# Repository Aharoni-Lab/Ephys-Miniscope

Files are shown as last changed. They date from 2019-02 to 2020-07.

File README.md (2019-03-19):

## Tutorial for assembling and using the integrated ephys Miniscope

Here we discuss the setup for the E-Scope. Below outlines the steps involved in assembling the head-mounted portion and DAQ portion of the system.

## Head-mounted E-Scope soldering and assembly

#### Components that need to be bought

* [Atmel ICE](https://www.digikey.com/products/en?mpart=ATATMEL-ICE&v=150) for programming the wire-free PCB
* Mill-Max 50mil male and female headers. You can get these from digikey.com and they are used to connect the INTAN PCB to the CMOS PCB. These are optional and generally should be skipped for mice.

#### Software to download
* Download [Atmel Studio](https://www.microchip.com/mplab/avr-support/atmel-studio-7). This will be used to program the microcontroller firmware onto the CMOS PCB.
* Downloaod the [Intan RHD2000 Interface Software](http://intantech.com/files/RHD2000interface_compiled_v1_5_2.zip). This will be used to connect and record ephys data.

### 1) Soldering wires to connect the CMOS PCB to the INTAN PCB

We first need to wire up 5 wires on the CMOS PCB. You should use very thing wiring for this (~0.25mm diameter conductors) since some of these connections will attach directly to the side pad of the serializer chip. You can use very thing "wire-wrap" wire which is single core or you can use mutlicore wire. Single core has the advantage of not splaying out but it is also less flexible. Once soldered, you should lay all 5 wires down across the top of the serializer and epoxy them (with a PCB safe glue/epoxy) so that no strain is applied to the solder connections. 

Below is a picture of the locations to solder the 5 wires. 
* D10 and D11 will carry the SSC Clock and SSC Data lines. 
* PCLK carries the pixel clock which will drive the SSC data protocol out of the INTAN PCB. 
* Finally, V+ and GND will provide power to the INTAN PCB.

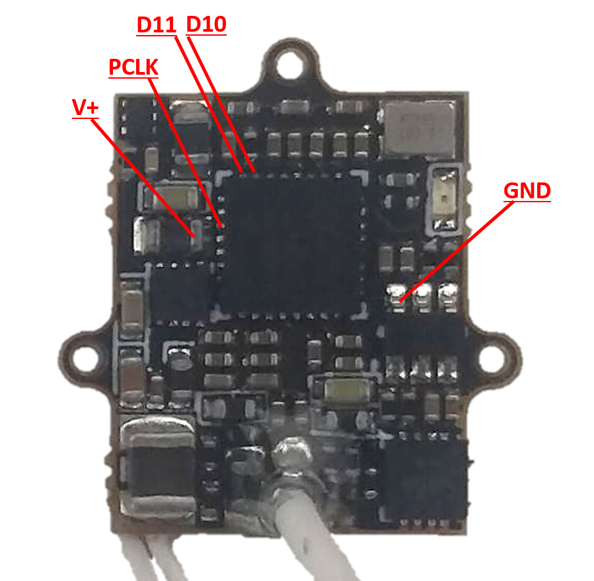
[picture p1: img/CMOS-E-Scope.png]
CMOS PCB wiring


### 2) Soldering wires onto the INTAN PCB

Now we need to solder the wires coming off the CMOS PCB onto the INTAN PCB. We have the choice to either directly solder these wires or to place a MillMax 50mil pitch header on these pads to connectorize them. For mice I would suggest directly soldering to minimize size and weight.

For connecting to the CMOS PCB v3.2 you will do the following connections (shown in the image below:
* GND connects to GND
* MCU V+ connects to V+
* INTAN V+ connects to V+
* SSC DATA connects to D10 or D11 (either is fine but keep this consistent across the E-Scopes you assemble
* LV can be left unconnected
* SSC Clock connects to PCLK
* SSC FRAME connects to D10 or D11 (use which ever one you didn't connect SSC DATA to)

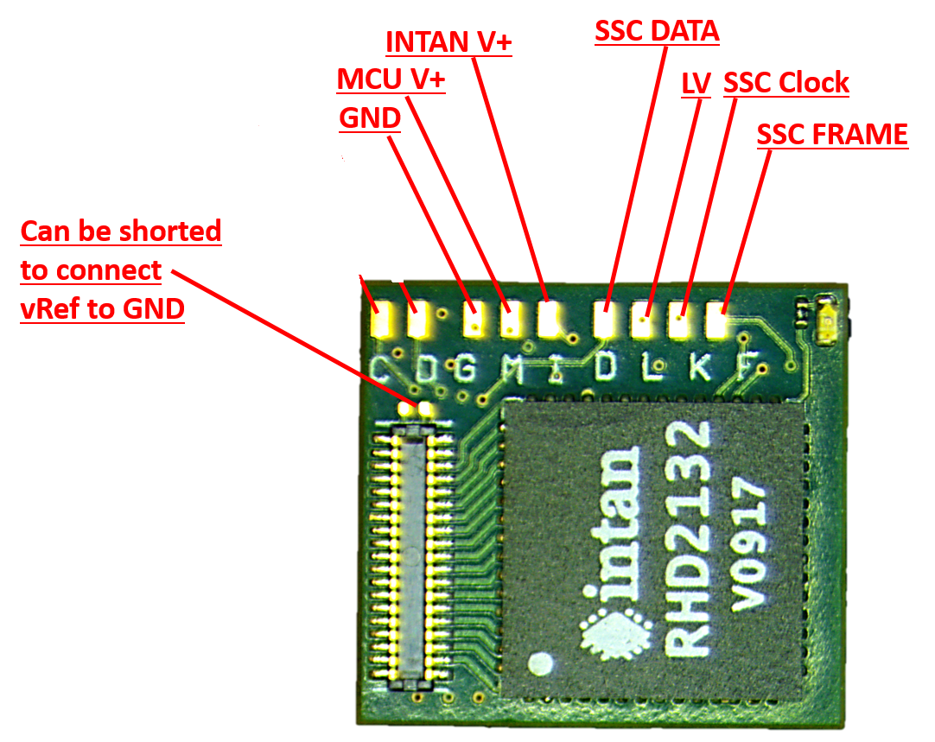
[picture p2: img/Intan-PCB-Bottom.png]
INTAN PCB wiring_bottom


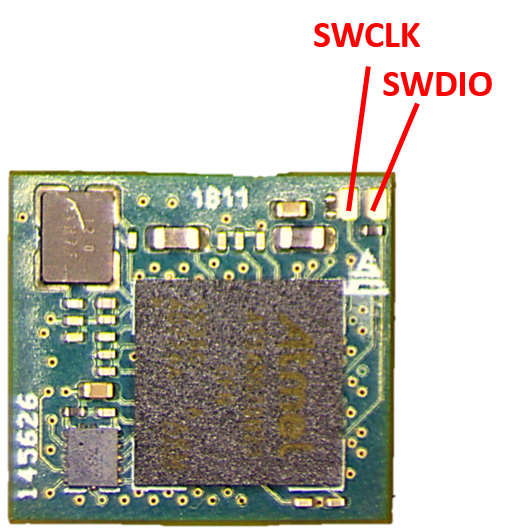
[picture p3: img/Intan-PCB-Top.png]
INTAN_PCB_wiring_top


### 3) Programming the MCU on the INTAN PCB

On one side of the INTAN PCB is the Intan RHD2132 chip and the other side is an ARM Cortex microcontroller (MCU). This MCU needs to be programmed once with the E-Scope firmware before it is functional. To do this we need to connect 4 lines to the INTAN PCB. This can, and maybe should, be done before completing step 2 above. The advantage of doing this programming step after completing step 2 above is the INTAN PCB can be powered through the coax cable and no additional power supply is needed.

You need to connect the following lines (refer to the images in step 2):
* SWCLK
* SWDIO
* MCU V+
* GND

These 4 lines need to be connected to an Atmel ICE which is the hardware necessary to program the MCU using an SWD protocol.
* In order to program the microcontroller on the INTAN  PCB, we first need to wire-up and connectorize a 4pin Mill-Max header to the 4 programming pins of the Atmel ICE programmer. These are GND, VTG (or V+), SWDIO, and SWDCLK. Below shows which pins/wires of the Atmel ICE have which function. The Atmel ICE has 2 different 5x2 pin ports. One is labeled AVR and one is labeled SAM. Either will work but depending on which one you are using it will change which column you refer to in the below chart.
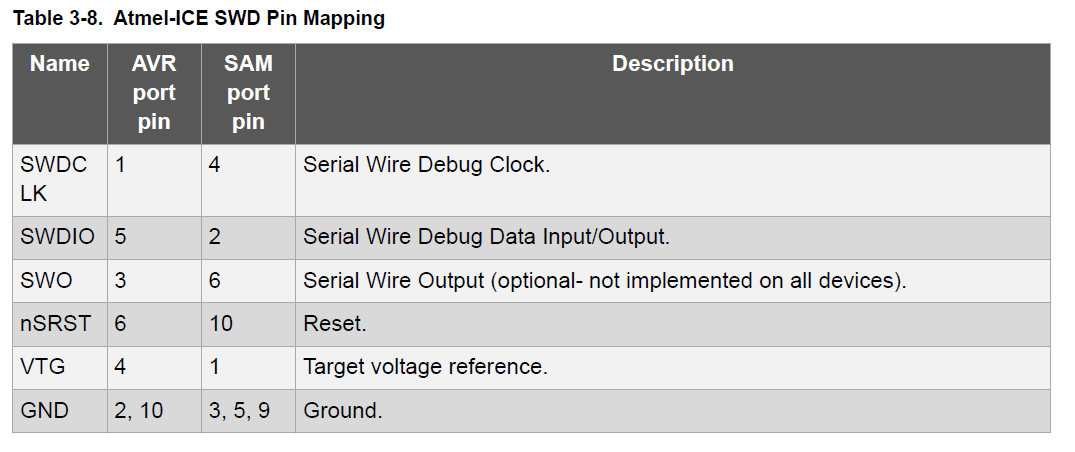
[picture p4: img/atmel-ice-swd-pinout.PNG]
Atmel ICE SWD pinout

* Connect the Atmel ICE to the programming header of the INTAN PCB.
* Power up the INTAN PCB throught either the coax cable (using the Miniscope DAQ) or directly connect 3.3V and GND from a power supply to the V+ and GND pads. 
* When the INTAN PCB gets powered on, you should see an orange light turn on on the Atmel ICE which shows that the Atmel ICE has detected voltage on the VTG (Voltage Target) pin.
* Open Atmel Studio and click the "Device Programming" button
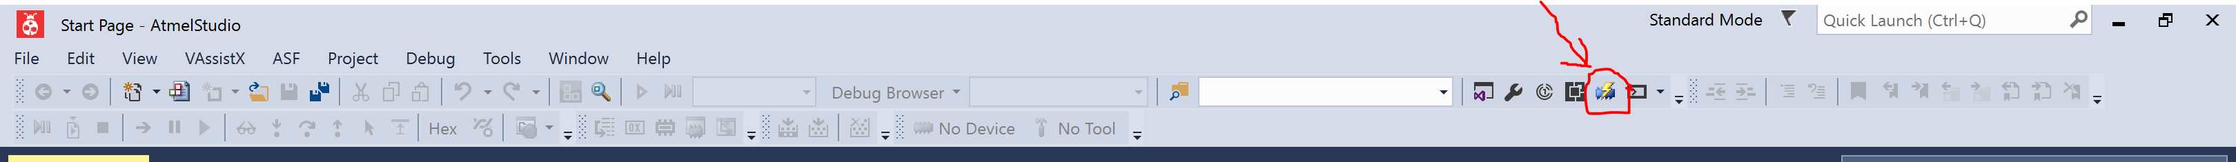
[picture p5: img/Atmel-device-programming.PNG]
Atmel Studio device programming buttone

* In the Device Programming window that pops up select:
  * Tool: Atmel ICE
  * Device: ATSAM....
  * Interface: SWD
  * Then click "Apply"
* Now check to make sure that Atmel Studio can communicate with the microcontroller on the INTAN PCB. You do this by clicking the "Read" button under Device Signature. If everything is powered and connected correctly you should see some numbers and letter pop up in the box and no error window show up. Now we are ready to program the microcontroller.
* Exit the Device Programming window.
* Now we have to do something a bit weird. I am not sure why this has to be done but it does. Open up the Atmel project found in the "/E-Scope-firmware" folder. This load up the code that makes up the INTAN MCU firmware. Now click "Debug" from the top menu bar and then click "Start Debugging and Break". Wait about 15 seconds while the debugger does its thing in Atmel Studio and then the code should jump to the "main()" function and highlight it. Now click the play button (labelled "Start Debugging") in the top menu. Wait a few seconds then click the stop button (labelled "Stop Debugging"). 
* Go back to the "Device Programming" window by clicking the "Device Programming" button.
* Click "Memory" on the left menu panel of the Device Programming window we are currently in.
* Click "Browse" and locate the E-Scope firmware. This is a .hex file you can find in the "/E-Scope-firmware" folder.
* Click "Program". This will erase, program, and verify the microcontroller. It will tell you if everything was successful.
* Now the microcontroller on the INTAN PCB knows how to be a wire-free Miniscope microcontroller.

## Miniscope DAQ E-Scope soldering and assembly

We now need to modify the standard Miniscope DAQ to be able to handle and transmit the ephys data from the E-Scope. We will do this by soldering 4 wires onto the DAQ PCB which will send the ephys data from the Miniscope DAQ to our SSC to INTAN LVDS PCB. We will roughly be following the following schematic:

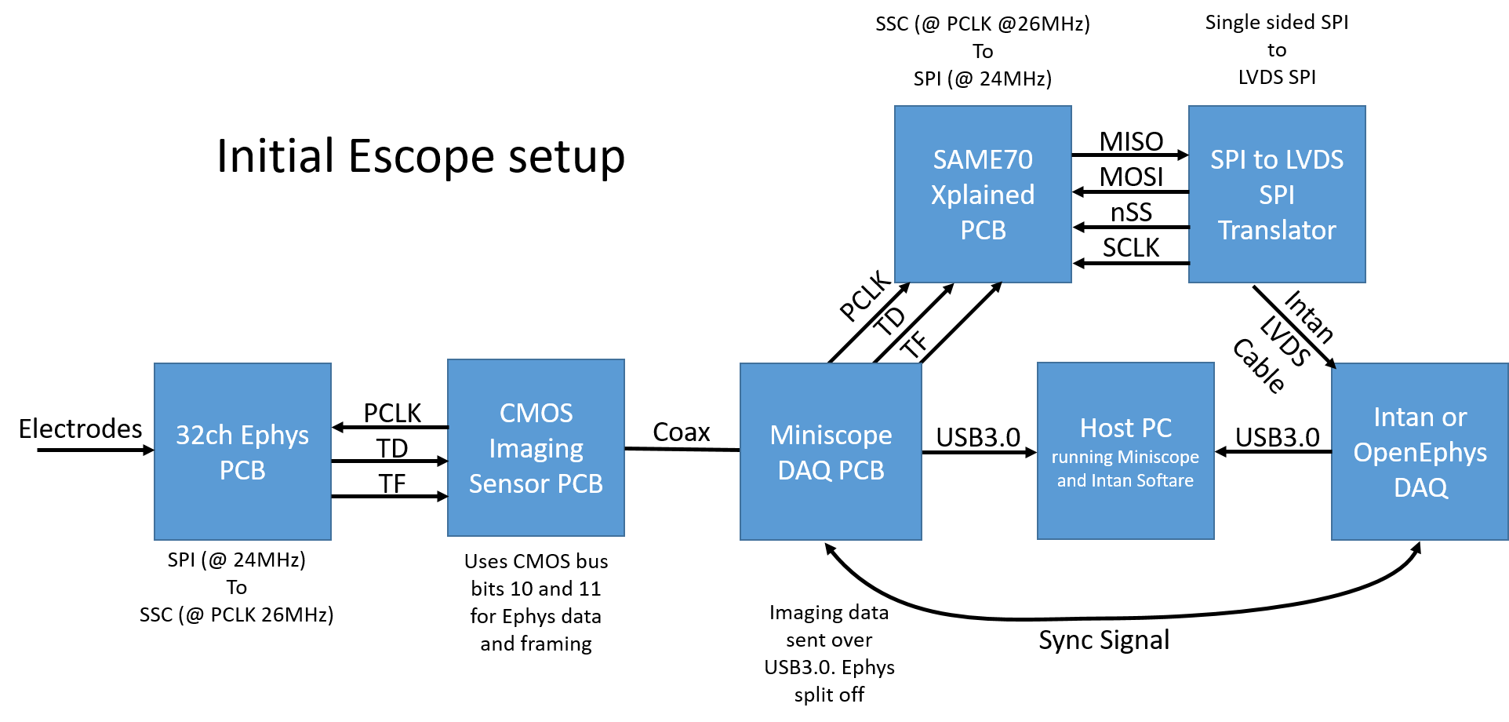
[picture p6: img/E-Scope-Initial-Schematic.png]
E-Scope Schematic


As you can see from the schematic, these wires coming off of the Miniscope DAQ PCB will connect to hardware that basically undoes the SSC data protocol implemented by the MCU on the INTAN PCB and make an Intan DAQ think that it is talking directly to an Intan headstage.

### 1) Wire up the Miniscope DAQ PCB

Similar to what we did for wiring up the CMOS PCB, we need to wire up some lines for SSC DATA, SSC Clock, SSC FRAME, and power. See image below for which pads to solder to. Use the same wire as you used to wire up the CMOS PCB and epoxy these wires down to the DAQ PCB to remove any strain on the solder joints.

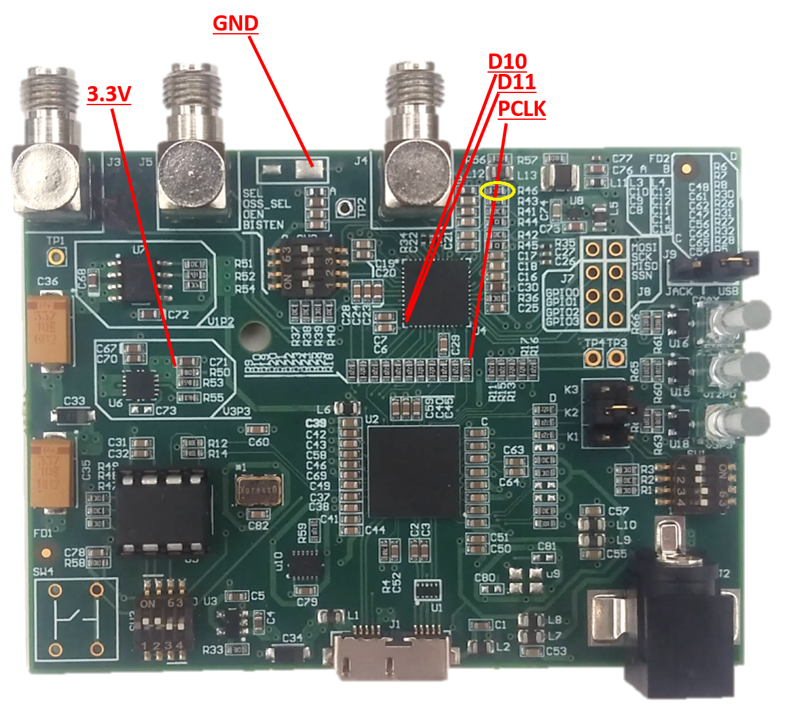
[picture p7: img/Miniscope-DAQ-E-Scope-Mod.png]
Miniscope-DAQ-E-Scope-Mod


You definitely need to solder up D10, D11, PCLK, and GND. The need for the 3.3V connection will depend on which version of the system you are using. You might as well just solder this one up as well.

### 2) Change the Miniscope DAQ Deserializer Mode from 10 bits to 12 bits

We need to remove one resistor on the Miniscope PCB and short then now empty pads together . This resistor is responsible for change the Deserializer from using 10bit mode to 12bit mode. We need to do this because the CMOS imaging sensor uses the bottom 10 bits of the SERDES and the Ephys data uses the top 2 bits (TD, TF which are on pins D10 and D11). So **remove resistor R46 (which is circled in yellow above)** which is near the top of the PCB to the right of the SMA connector that goes to the head-mounted scope. Once you remove this resistor, we need to short the 2 open pads together which effectively changes this resistance to 0 ohms. You can build up a solder ball that spans these 2 pads, solder a short piece of metal across these 2 pads, or solder a 0ohm resistor in the R46 location. I recommend the last option.

### 3) Connect the Miniscope DAQ PCB to SSC-2-INTAN-LVDS PCB

Alright, we are almost done here. The ephys data coming out of the wires we soldered onto the Miniscope DAQ need to get converted to a data protocol an Intan DAQ understands. We do this using our custom SSC-2-INTAN-LVDS PCB. This PCB receives SSC (RF,RT,RK) and converts it to an LVDS SPI to be sent out over a 2x6 omnetics connector at the top of the PCB to an Intan or OpenEphys DAQ. Below is a rendering of this PCB.

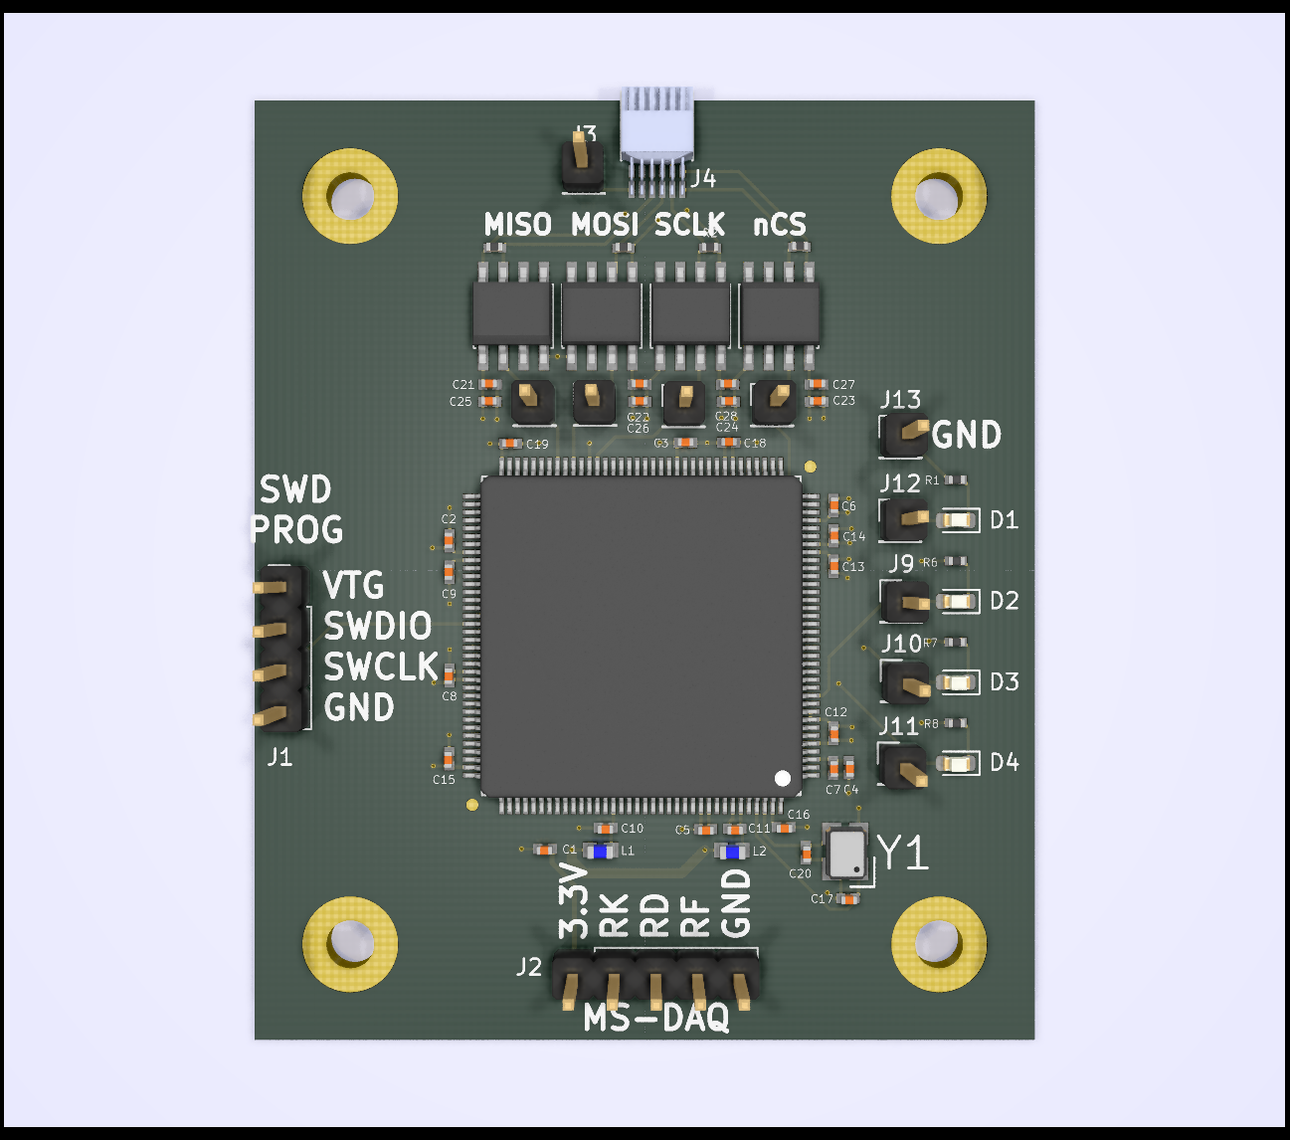
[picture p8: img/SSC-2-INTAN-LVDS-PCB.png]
SSC-2-INTAN-LVDS


At the bottom of this board is a 5 pin 100mil pitch header for connecting it to the Miniscope DAQ. I would suggest soldering a right angle header to this PCB pointing down. On the Miniscope DAQ, you can epoxy another 5 pin header to the edge of the PCB so that these 2 PCBs can be easily connected. The connections need to be the following:

**NOTE**

**For the original version of this PCB, the labelling is incorrect.** The order should 3.3V, RD, RF, RK, GND and not 3.3V, RK, RD, RF, GND.

| SSC-2-INTAN PCB | Miniscope DAQ PCB |
| --- | --- |
| GND | GND |
| 3.3V | 3.3V |
| RK | PCLK |
| RD | D10 or D11. Whichever one was connected to TD on the 32 channel Ephys PCB|
| RF | D10 or D11. Whichever one was connected to TF on the 32 channel Ephys PCB |

### 4) Program the MCU on the SSC-2-INTAN-LVDS PCB

Out last step is to program this PCB so it knows what it is suppose to do. Here we follow the same procedure we did above for programming the 32 Channel Ephys PCB. The programming header on the SSC-2-INTAN-LVDS PCB is on the left and includes the 4 connections you need access to through a 100mil pitch header. These are VTG (which will tell the Atmel ICE programmer to program the MCU at 3.3V), SWDIO, SWCLK, and GDN. Follow the steps above but program this MCU with the SSC-2-INTAN-LVDS firmware .hex file. This PCB needs to be powered up when programming which is done through the bottom 'MS-DAQ' 5 pin header by supplying 3.3V and GND. If you already have this hooked up to the Miniscope DAQ all you should need to do is power up the Miniscope DAQ and it should in turn power on this PCB.

## Hook everything up and test the system

We should now be done with all the hard work. All that is left to do is connect everything together and make sure we are getting correct data from the system. The overall layout should be:

32 Channel Ephys PCB -> CMOS sensor PCB -> coax -> Miniscope DAQ -> SSC-2-INTAN-LVDS PCB -> Intan or Open Ephys DAQ

All the power on all of these PCBs is floating which apperently introduces a ton of noise. **To fix this we need to connect building ground to the ground of the Miniscope system. This can be most easily done (be careful) by plugging in only the ground pin of an electrical cord into a wall electical socket and then clip the other end of the ground wire of the cable to the pin labeled 'GND' on the SSC-2-INTAN-LVDS PCB. Do this before powering everything up.**

Once you have connected building ground you can plug in the USB cable of the Miniscope DAQ and the USB cable and power jack of the Intan DAQ. Now open up the Intan DAQ software on the computer and make sure it detects the Intan DAQ and a 32 channel headstage. Right now the Intan DAQ thinks it is talking to an Intan headstage but it is actually talking to the SSC-2-INTAN-LVDS PCB. If you leave the coax cable unconnected from the Miniscope DAQ you will see placeholder data show up in the Intan DAQ software. This should look like DC voltages on all 32 channels with channel 0 having the lowest voltage and channel 31 having the highests. Once the head-mounted Miniscope coax cable is connected, this placeholder data gets replaced with real ephys data.

**A few important notes:**

* Generally you will want the ephys and imaging synced together. This is done by connecting one of the Intan DAQ digital input ports to the SYNC output of the Miniscope DAQ (which is the SMA connector labeled J5). Make sure to enable this digitial input pin in the Intan DAQ software. This will result in the Intan DAQ recording the SYNC signal from the Miniscope DAQ which will allow us to sync all the data offline. If you do this, **make sure to always start the Intan DAQ software recordinging before you start the Miniscope DAQ software recording.**

**Order of connecting and powering up the system**

* Hook up ground of the DAQ system to building ground
* Connect the Miniscope to Miniscope DAQ using the coax cable
* Hook up the DC power supply on the Intan DAQ
* Hook up the two USB cables. One for the Miniscope DAQ and one for the Intan DAQ
* Make sure that the sync cable is connected (Cable that connects the Intan board with the Miniscope DAQ)
* Open up Intan DAQ software and Miniscope DAQ software
* In the Intan software, click "Board Digital Inputs" radio button. Then turn on LOGIC DIN-00.
* Check everything is running correctly by clicking the "Runn" button in the Intan software and by connecting to the Miniscope using the Miniscope DAQ software.

**When ready to record**
* In the Intan software, click the "Select Vase Filename" button and name the ephys recording file.
* Click record in the Intan software
* Click record in the Miniscope DAQ software
* Do your recording
* Stop recording with the Miniscope DAQ software
* Stop recording with the Intan software

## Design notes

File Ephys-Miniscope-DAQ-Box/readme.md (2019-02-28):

3D printer model for Ephys-Miniscope DAQ box

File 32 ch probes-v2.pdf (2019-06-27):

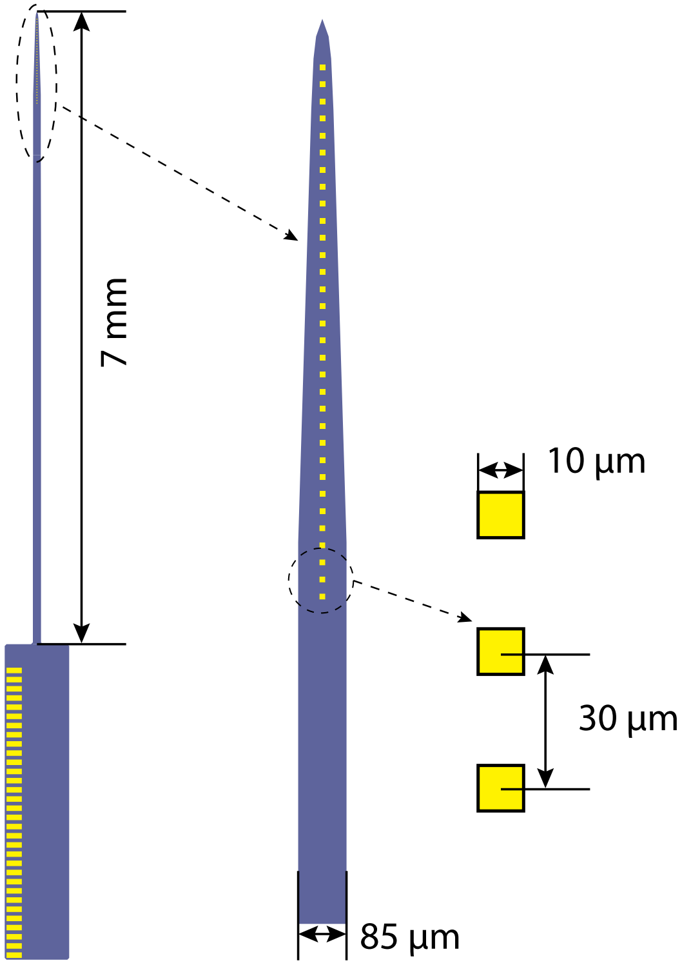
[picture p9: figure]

32ch probe geometry

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
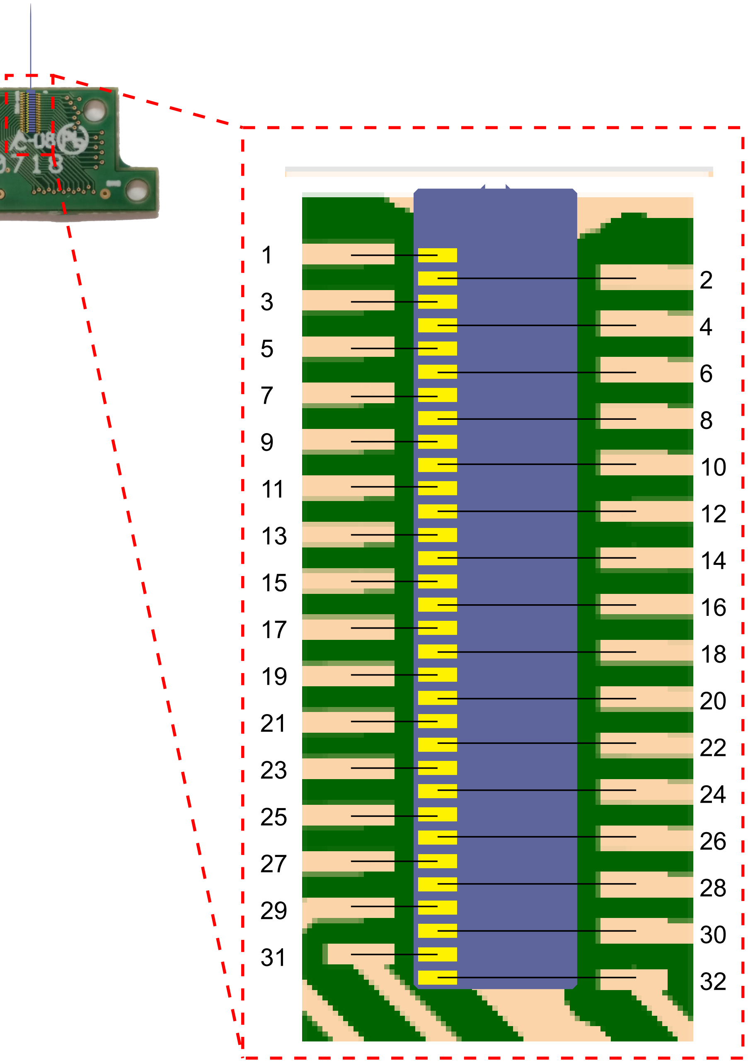
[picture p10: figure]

Channel number definition and corresponding Pin number

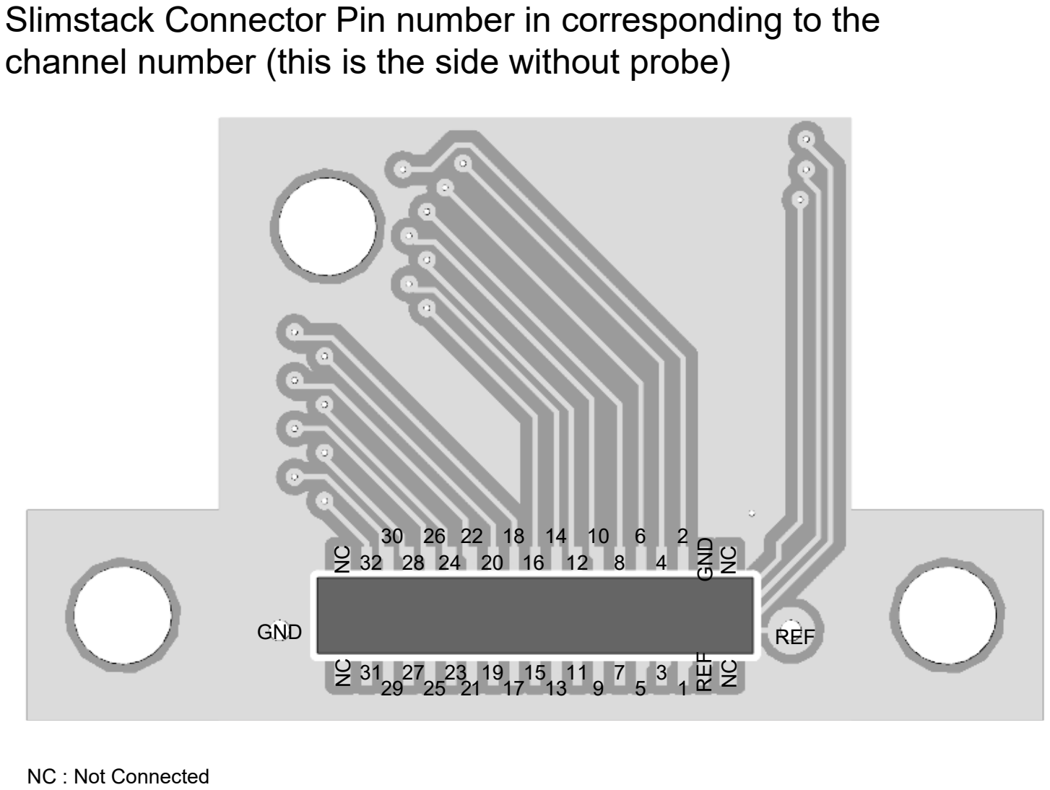
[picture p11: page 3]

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
GND | REF

Slimstack Connector Pin number in corresponding to the channel number (this is the side without probe) NC NC NC NC

NC : Not Connected

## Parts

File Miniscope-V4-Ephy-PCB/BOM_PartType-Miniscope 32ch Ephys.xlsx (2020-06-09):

Comment | Manufacture Part Number | Digikey Part Number | Description | Designator | Footprint | LibRef | Quantity | Value
Capacitor | GRM155R60J475ME47D | 490-5915-1-ND | Generic SMD Capacitor | C1, C3 | CAPC100X50X60L25N | Capacitor | 2 | 4.7uF
Capacitor | GRM033R61A104ME15D | 490-5405-1-ND | Generic SMD Capacitor | C2, C4, C5, C6, C7, C9, C10, C12, C13, C16 | CAPC60X30X33L15L | Capacitor | 10 | 100nF
Capacitor | GRM033R61A105ME15D | 490-13226-1-ND | Generic SMD Capacitor | C8 | CAPC60X30X33L15L | Capacitor | 1 | 1uF
Capacitor | GRM033R71A103KA01D | 490-3194-1-ND | Generic SMD Capacitor | C14, C15 | CAPC60X30X33L15L | Capacitor | 2 | 10nF
Capacitor | GRM0335C1H120JA01D | 490-6114-1-ND | Generic SMD Capacitor | C17, C18 | CAPC60X30X33L15L | Capacitor | 2 | 12pF
LED | VLMS1500-GS08 | VLMS1500-GS08CT-ND | LTST-C191KRKT | D1 | 0402 LED | LXZ1-PR01 | 1
34Pin Connector | 5046223410 | WM10896CT-ND | 34Pin Connector | J1 | 504622-3410 | 16x2 Pin Molex | 1
Inductor | BLM18PG471SN1D | 490-5223-1-ND | Generic SMD Inductor | L2, L3 | INDC160X80X95L40L | Inductor SMD | 2 | 470 Ohms @ 100MHz
Res1 | DO NOT LOAD | DO NOT LOAD | Generic SMD Resistor | R1 | RESC60X30X26L15L | Resistor | 1 | DNL
Res1 | ERJ-1GEF2002C | P20.0KABCT-ND | Generic SMD Resistor | R2 | RESC60X30X26L15L | Resistor | 1 | 20kOhm
Res1 | ERJ-1GEF1003C | P100KABCT-ND | Generic SMD Resistor | R3, R4 | RESC60X30X26L15L | Resistor | 2 | 100kOhm
Res1 | RC0201FR-07499RL | YAG2700CT-ND | Generic SMD Resistor | R5 | RESC60X30X26L15L | Resistor | 1 | 499Ohm
SAMS70N21 | ATSAMS70N21A-CFNT | 1611-ATSAMS70N21A-CFNTCT-ND | SAMS70N21 ARM Cortex-M | U1 | VFBGA100CP65_10X10_700X700X100B32L | SAMS70N21 | 1
RHD2132 | RHD2132. I will supply this component | I will supply this component | Intan Technologies RHD2132 | U2 | QFN57P50_800X800X85L40X23T610L | RHD2132_QFN | 1
ABM8G-12.000MHZ-4Y-T3 | ABM8G-12.000MHZ-4Y-T3 | 535-10901-1-ND | ABM8G-12.000MHZ-4Y-T3 | U3 | ABM8G-12.000MHZ | ABM8G | 1
TXB0304 | TXB0304RUTR | 296-29682-1-ND | TXB0304 4ch bidir. level shift 100Mbps | U4 | QFN12 | TXB0304 | 1

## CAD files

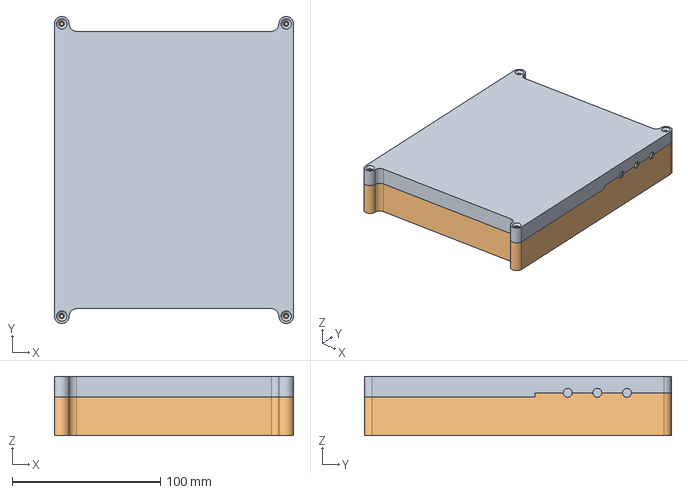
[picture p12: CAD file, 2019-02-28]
Ephys-Miniscope-DAQ-Box/Board Base v30.step
161.3 x 207.0 x 40.0 mm

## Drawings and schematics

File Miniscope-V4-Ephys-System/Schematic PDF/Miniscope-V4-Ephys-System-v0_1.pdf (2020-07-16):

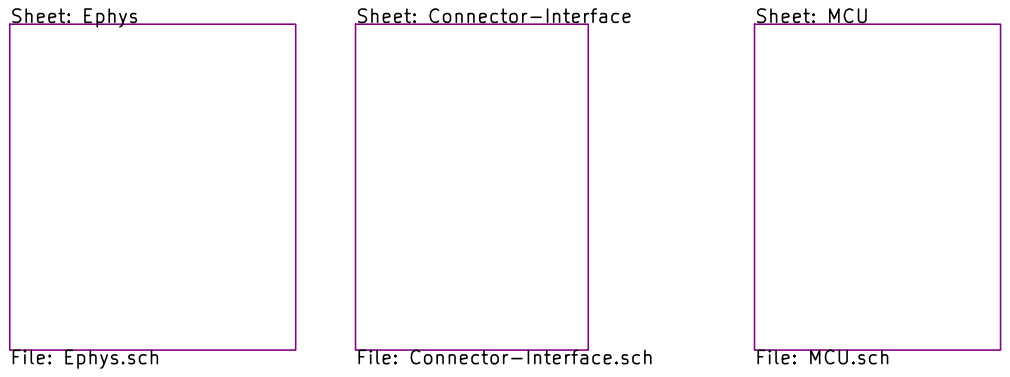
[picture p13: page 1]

File: Miniscope-V4-Ephys-System.sch Sheet: / Daniel Aharoni

Id: 1/4 Title: E-Scope System

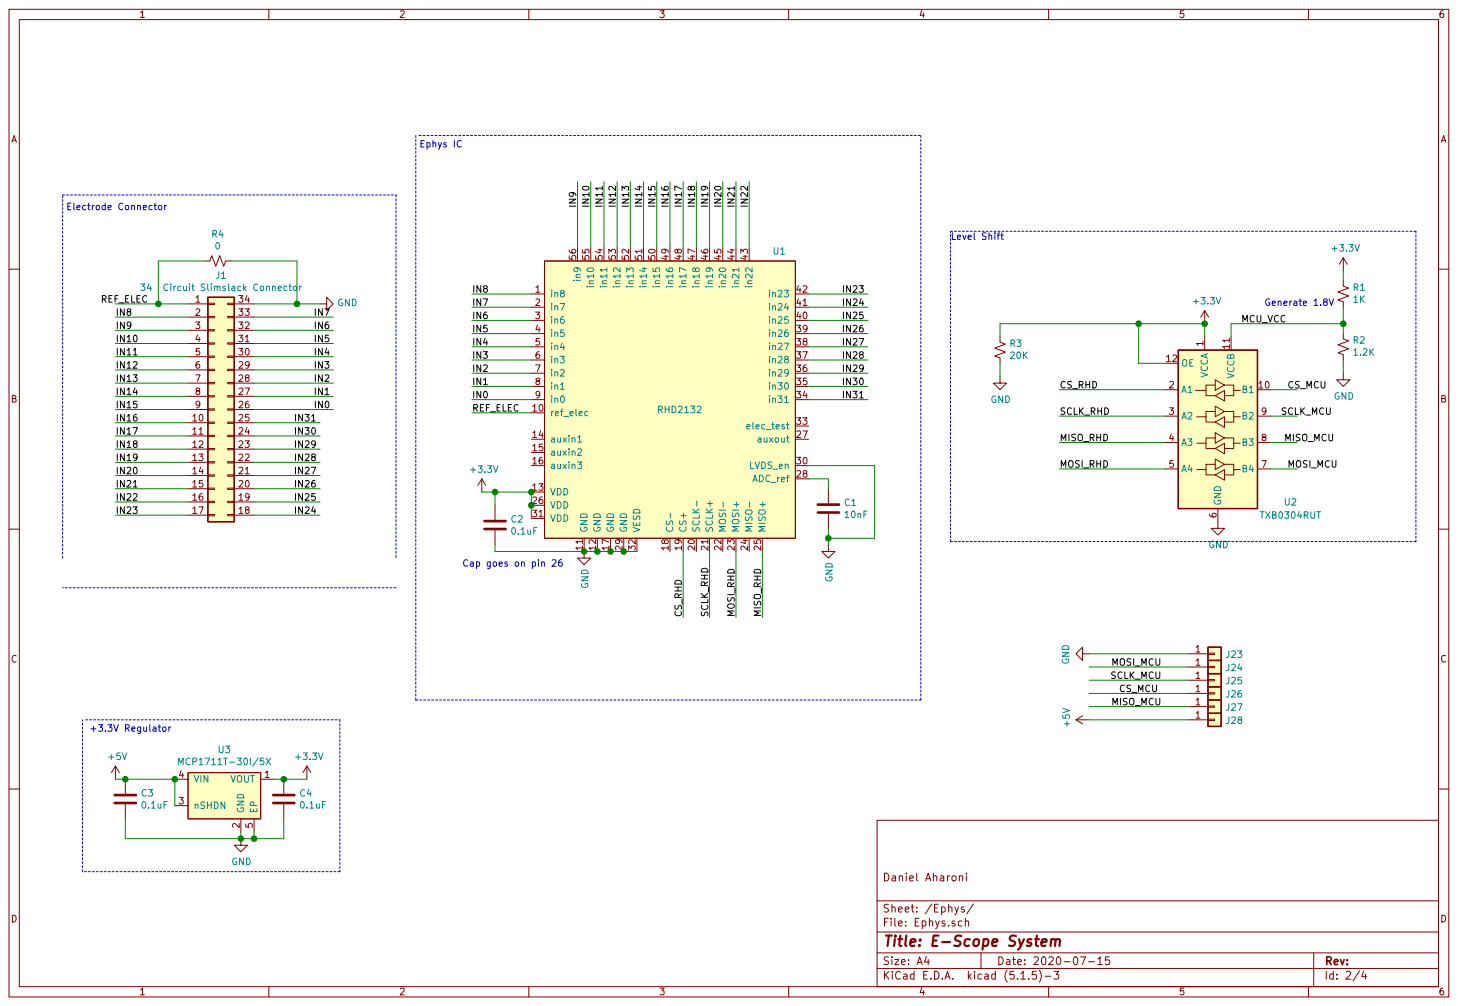
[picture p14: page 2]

Level Shift Electrode Connector

Cap goes on pin 26

Sheet: /Ephys/ Daniel Aharoni

File: Ephys.sch
Id: 2/4 Title: E-Scope System

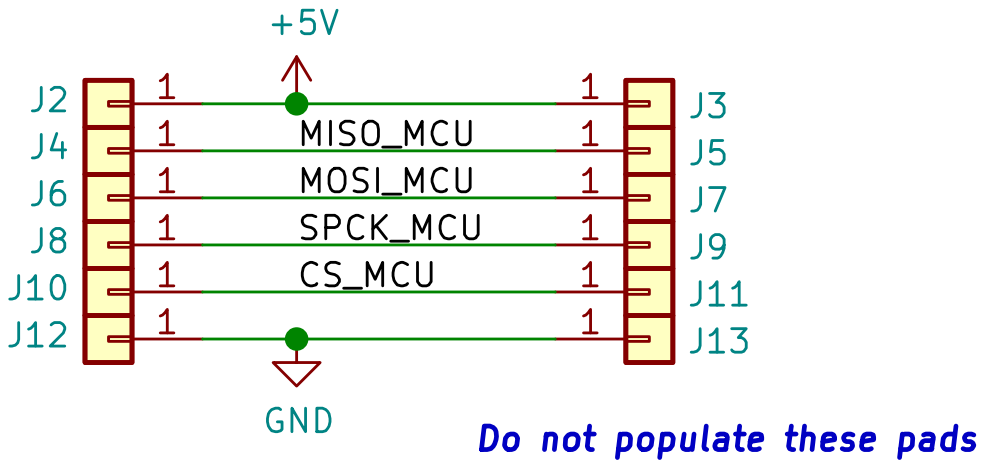
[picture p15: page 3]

Do not populate these pads

File: Connector-Interface.sch Sheet: /Connector-Interface/ Daniel Aharoni

Id: 3/4 Title: E-Scope System

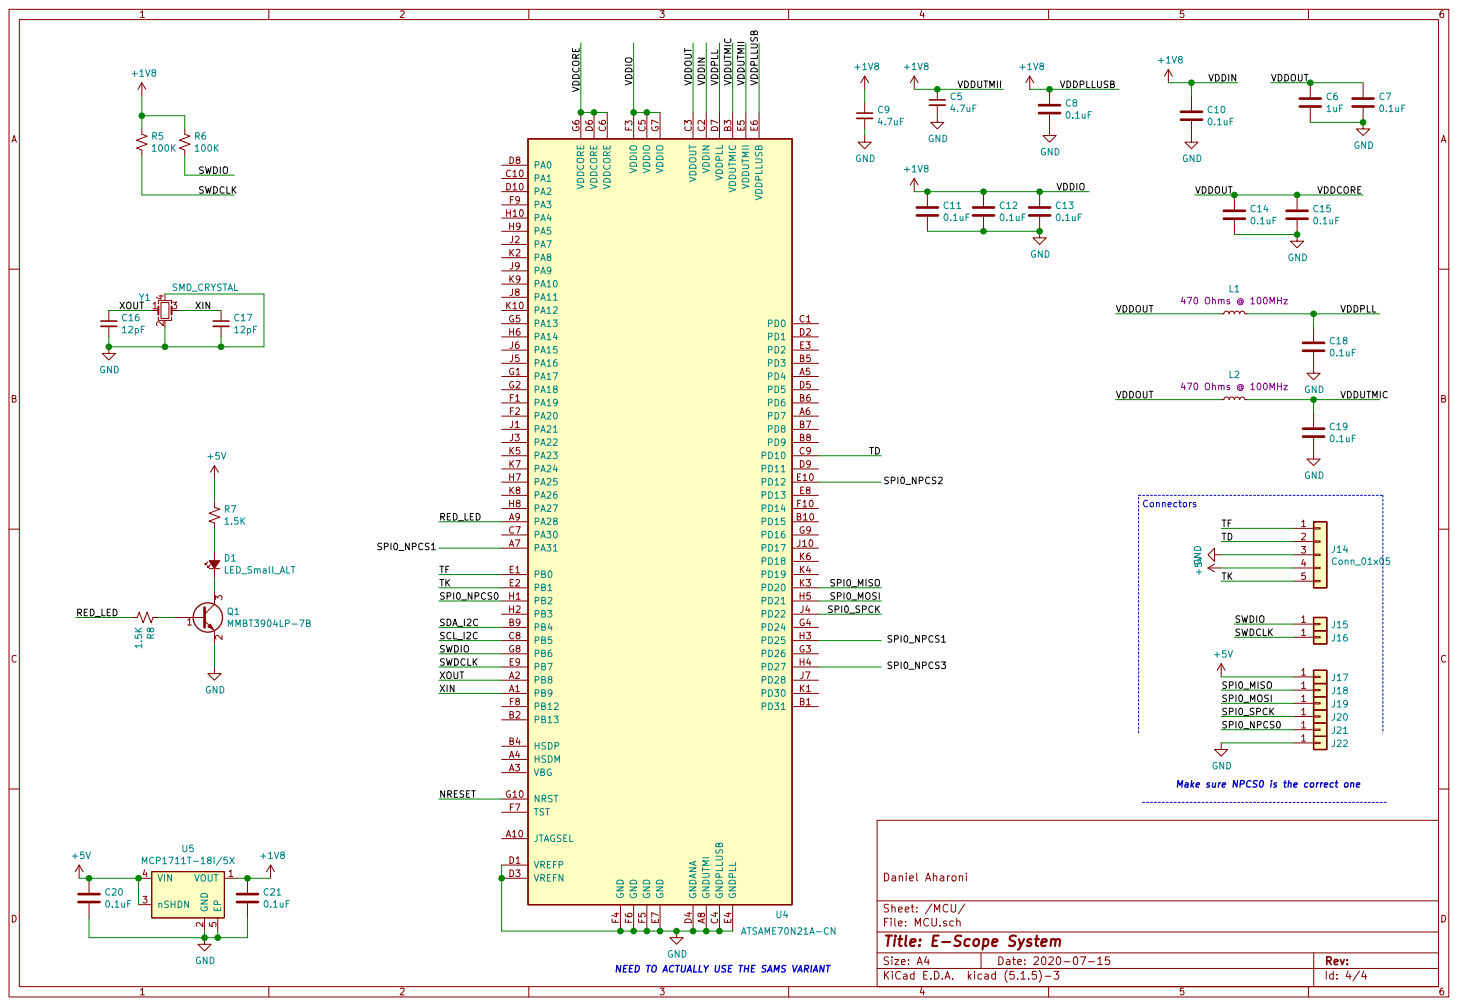
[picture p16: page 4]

Connectors Make sure NPCS0 is the correct one

File: MCU.sch Sheet: /MCU/ Daniel Aharoni

Id: 4/4 Title: E-Scope System

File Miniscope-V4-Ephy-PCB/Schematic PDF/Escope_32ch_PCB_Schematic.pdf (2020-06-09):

TST F7 | VDDIO C⁵ VDDIO F³ VDDIO G⁷
JTAGSEL | A10 VDDCORE C⁶ VDDCORE D⁶ VDDCORE G⁶ VDDPLL D⁷ VDDUTMII E⁵

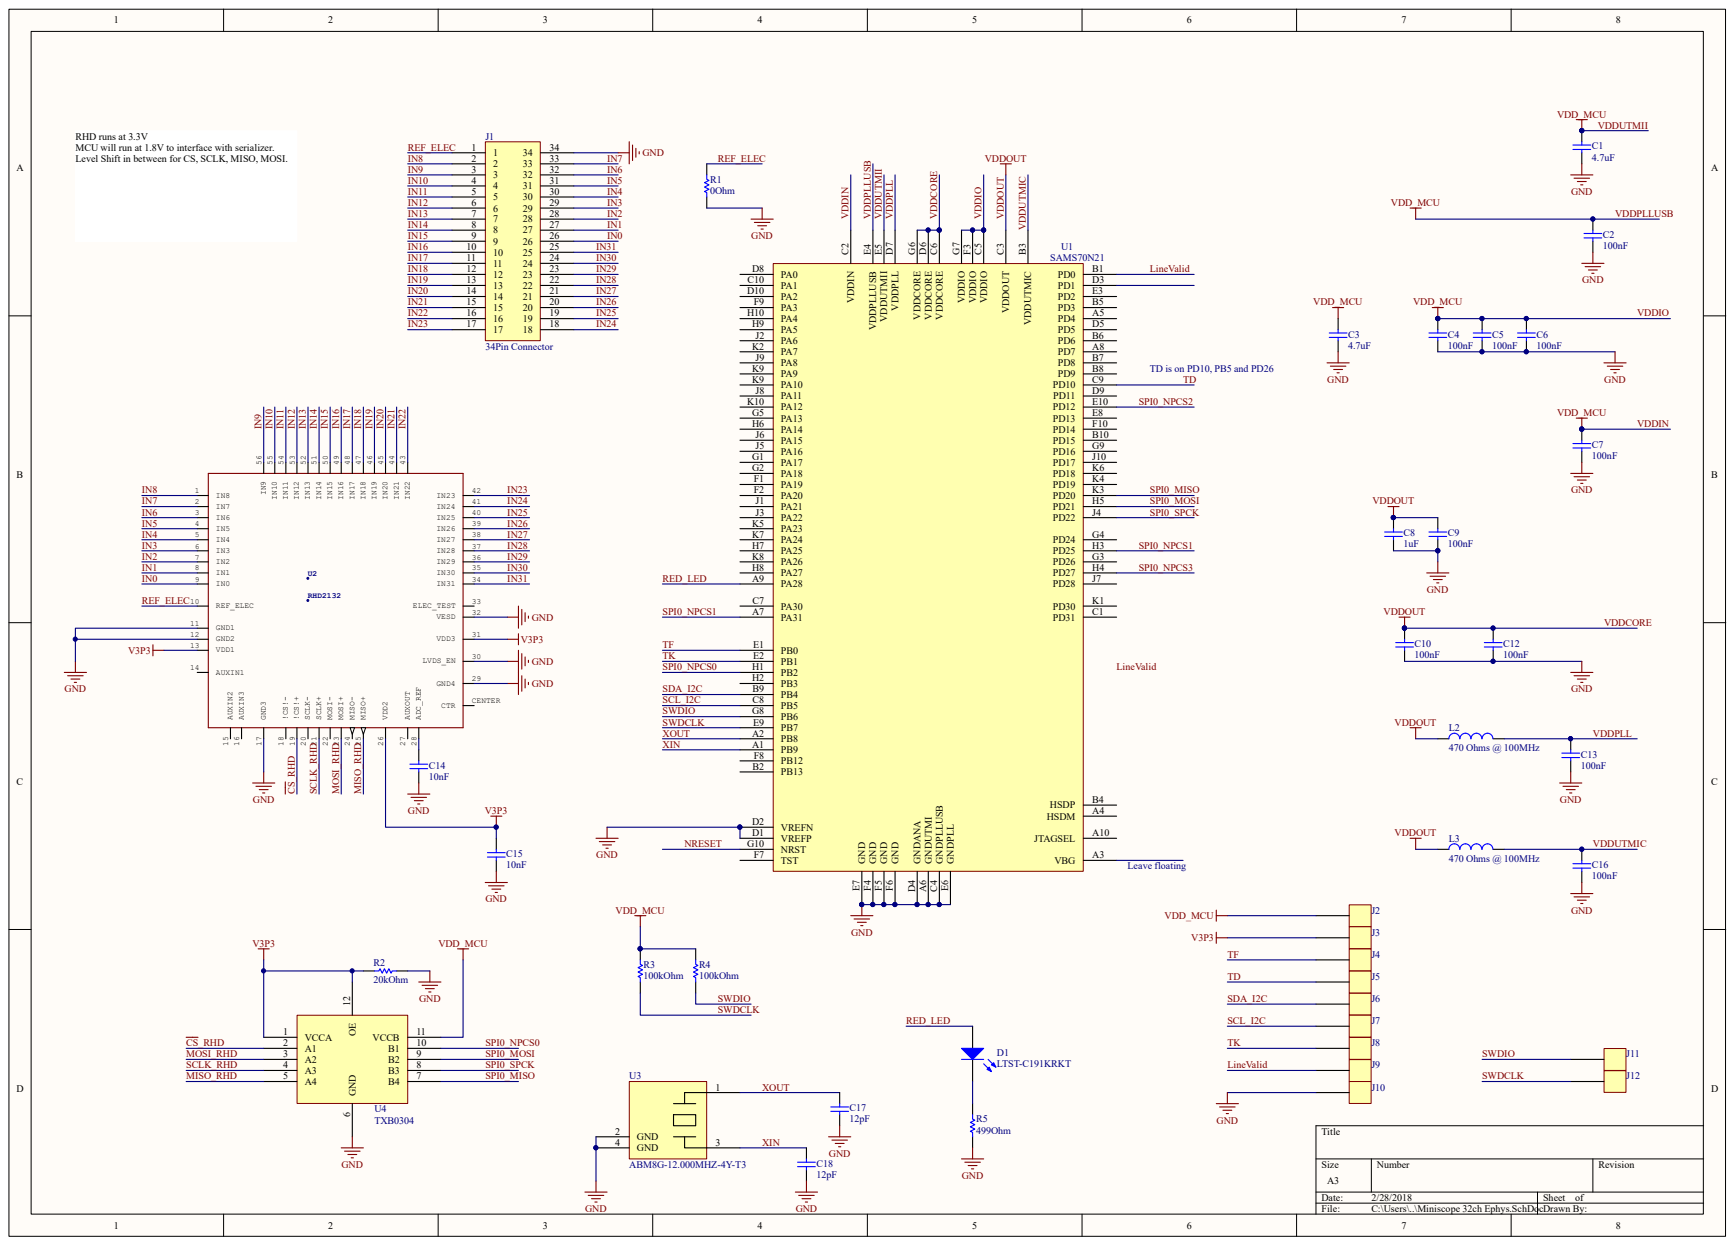
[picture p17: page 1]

RHD runs at 3.3V
MCU will run at 1.8V to interface with serializer.
Level Shift in between for CS, SCLK, MISO, MOSI.

TD is on PD10, PB5 and PD26

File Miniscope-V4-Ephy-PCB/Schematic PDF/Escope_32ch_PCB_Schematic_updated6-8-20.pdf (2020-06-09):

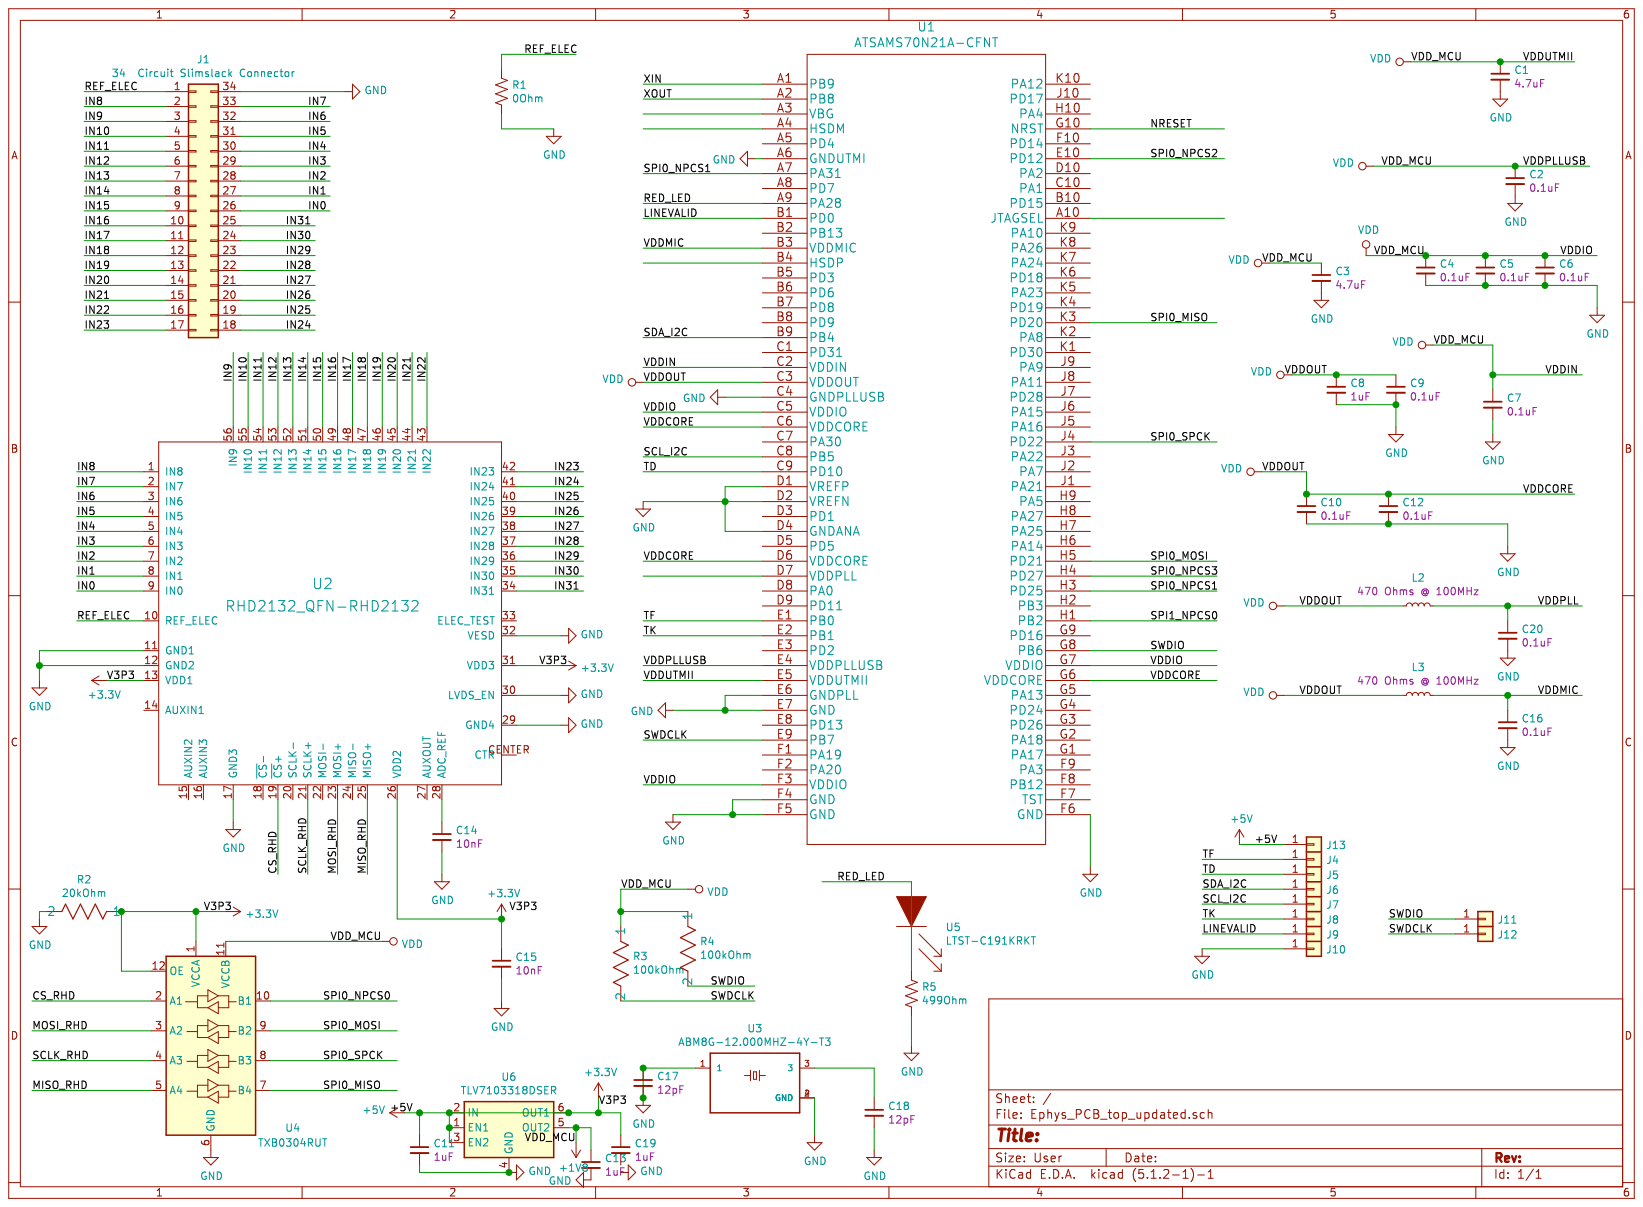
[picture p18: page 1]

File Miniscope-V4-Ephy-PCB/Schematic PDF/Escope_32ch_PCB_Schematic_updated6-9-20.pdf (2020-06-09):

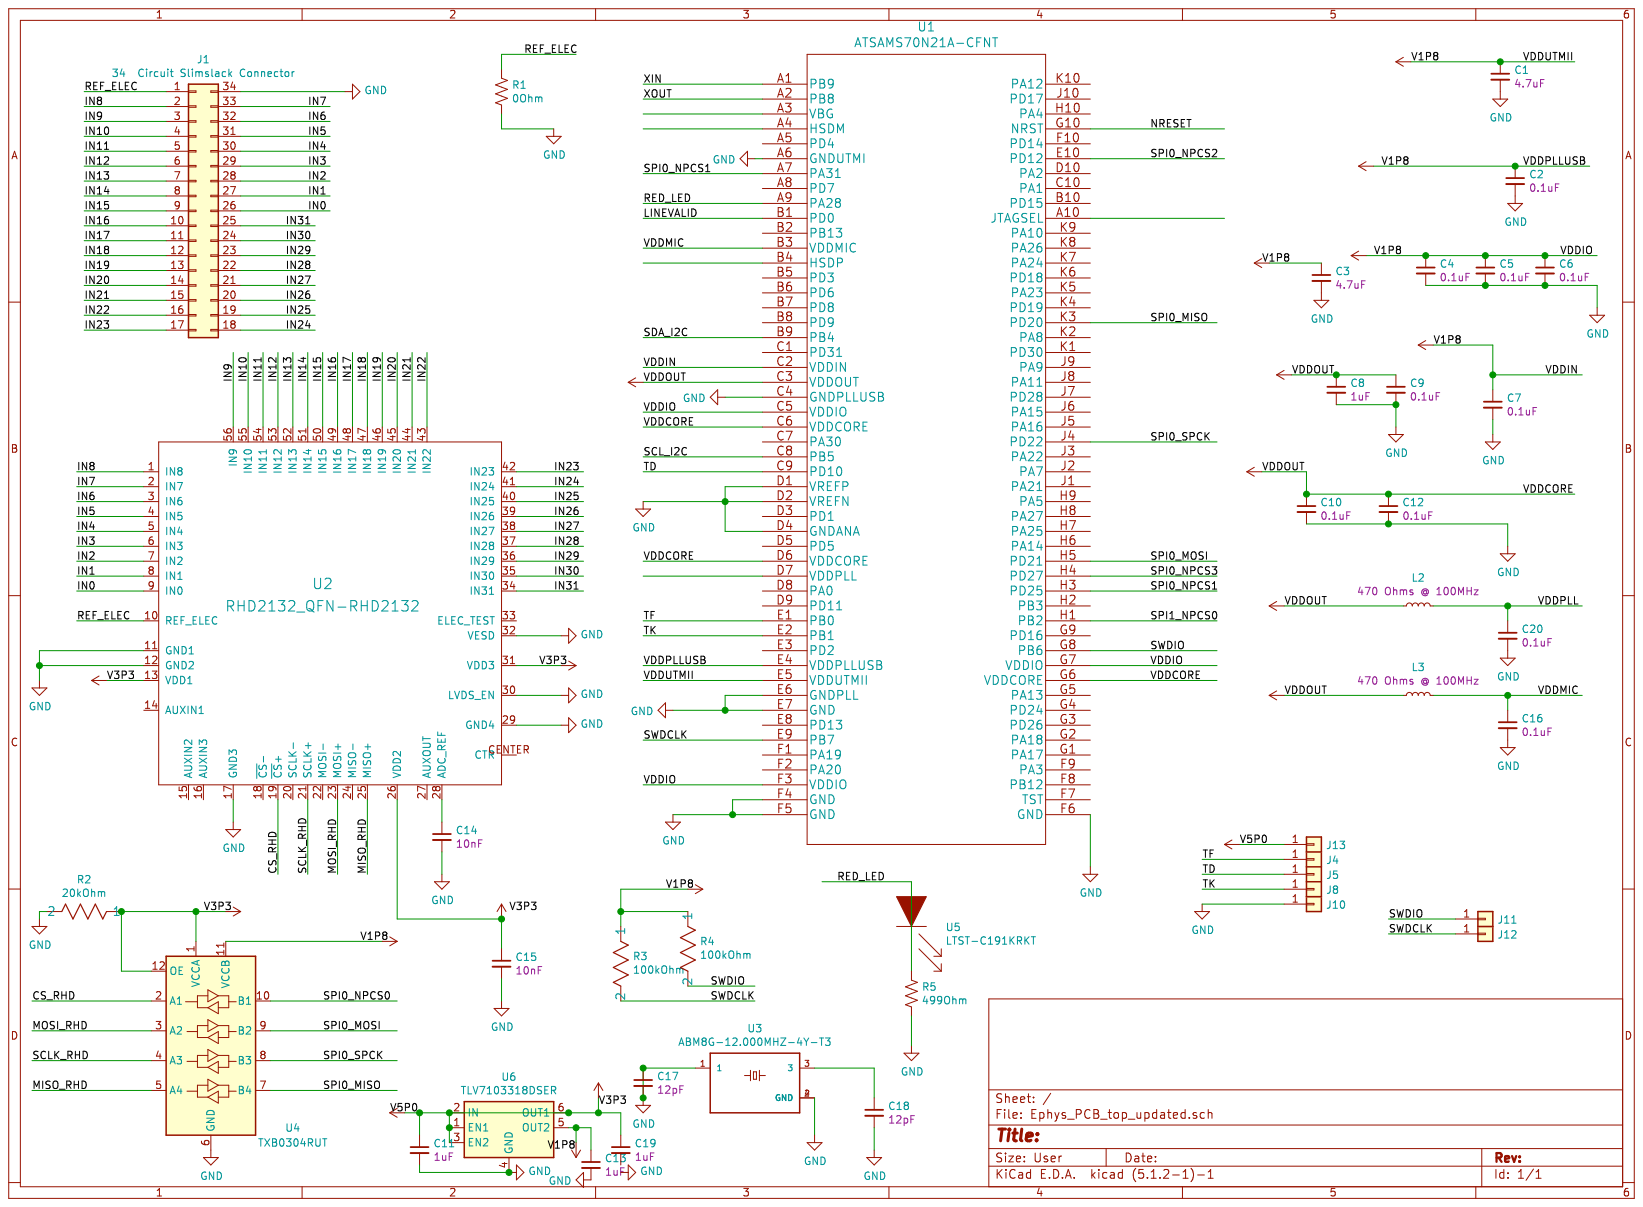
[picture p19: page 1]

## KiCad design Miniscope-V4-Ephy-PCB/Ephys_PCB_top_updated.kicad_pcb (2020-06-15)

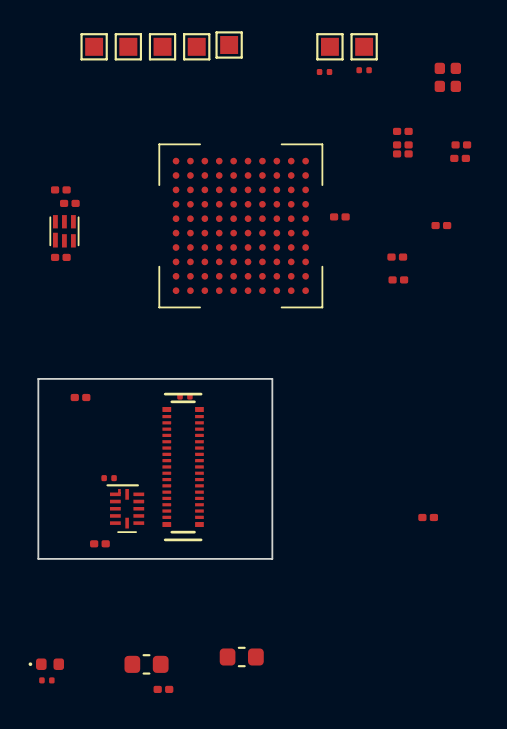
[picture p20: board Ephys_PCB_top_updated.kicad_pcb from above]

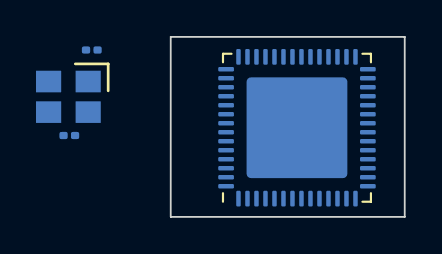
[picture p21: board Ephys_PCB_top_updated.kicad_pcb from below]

Board: 6 copper layers, 13.0 x 10.0 mm, 41 parts (4 on the bottom side), 60 nets, no tracks yet.

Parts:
C1, C3: 4.7uF; C_0402_1005Metric_L
C2, C4, C5, C6, C7, C9, C10, C12, C16, C20: GRM033R61A104ME15D; C_0201_0603Metric
C8, C11, C13, C17, C18, C19: GRM033R60J105MEA2D; C_0201_0603Metric
C14, C15: GRM033R71A103KA01D; C_0201_0603Metric
D1: LED_Small_ALT; LED_0402_1005Metric
J1: 34 Circuit Slimslack Connector; SS_5046223412
J4, J5, J8, J10, J11, J12, J13: Conn_01x01; TestPoint_Pad_1.0x1.0mm
L2, L3: BLM18PG471SN1D; L_0603_1608Metric
R1: 0; R_0201_0603Metric_ERJ_L
R2: 20K; R_0201_0603Metric_ERJ_L
R3, R4: 100K; R_0201_0603Metric_ERJ_L
R5: 499; R_0201_0603Metric_ERJ_L
U1: ATSAME70N21A-CN; BGA_100_CP80_10X10_900X900X110B40L
U2: RHD2132_QFN-RHD2132; QFN-56-1EP_8x8mm_P0.5mm_EP5.6x5.6mm
U3: TLV7103318DSER; SON_6_P50_150X150X80L50X25L
U4: TXB0304RUT; Texas_R_PUQFN-N12
Y1: ABM8G-12.000MHZ-4Y-T3; OSCCC320X250X100L80X100

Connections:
+1V8: C1.1, C2.1, C3.1, C4.1, C5.1, C6.1, C7.1, C13.1, R3.1, R4.1, U1.C2, U1.C5, U1.E5, U1.E6, U1.F3, U1.G7, U3.5, U4.11
+3V3: C15.1, C19.1, R2.2, U2.13, U2.26, U2.31, U3.6, U4.1, U4.12
+5V: C11.1, J13.1, U3.1, U3.2
/CS_RHD: U2.19, U4.2
/IN0: J1.27, U2.9
/IN1: J1.28, U2.8
/IN2: J1.29, U2.7
/IN3: J1.30, U2.6
/IN4: J1.31, U2.5
/IN5: J1.32, U2.4
/IN6: J1.33, U2.3
/IN7: J1.34, U2.2
/IN8: J1.1, U2.1
/IN9: J1.2, U2.56
/IN10: J1.3, U2.55
/IN11: J1.4, U2.54
/IN12: J1.5, U2.53
/IN13: J1.6, U2.52
/IN14: J1.7, U2.51
/IN15: J1.8, U2.50
/IN16: J1.9, U2.49
/IN17: J1.10, U2.48
/IN18: J1.11, U2.47
/IN19: J1.12, U2.46
/IN20: J1.13, U2.45
/IN21: J1.14, U2.44
/IN22: J1.15, U2.43
/IN23: J1.16, U2.42
/IN24: J1.19, U2.41
/IN25: J1.20, U2.40
/IN26: J1.21, U2.39
/IN27: J1.22, U2.38
/IN28: J1.23, U2.37
/IN29: J1.24, U2.36
/IN30: J1.25, U2.35
/IN31: J1.26, U2.34
/MISO_RHD: U2.25, U4.5
/MOSI_RHD: U2.23, U4.3
/RED_LED: D1.2, U1.A9
/REF_ELEC: J1.18, R1.1, U2.10
/SCLK_RHD: U2.21, U4.4
/SPI0_MISO: U1.K3, U4.7
/SPI0_MOSI: U1.H5, U4.9
/SPI0_NPCS0: U1.H1, U4.10
/SPI0_NPCS1: U1.A7, U1.H3
/SPI0_SPCK: U1.J4, U4.8
/SWDCLK: J12.1, R3.2, U1.E9
/SWDIO: J11.1, R4.2, U1.G8
/TD: J5.1, U1.C9
/TF: J4.1, U1.E1
/TK: J8.1, U1.E2
/VDDCORE: C8.1, C9.1, C10.1, C12.1, L2.1, L3.1, U1.C3, U1.C6, U1.D6, U1.G6
/VDDPLL: C20.1, L2.2, U1.D7
/VDDUTMIC: C16.1, L3.2, U1.B3
GND: C1.2, C2.2, C3.2, C4.2, C5.2, C6.2, C7.2, C8.2, C9.2, C10.2, C11.2, C12.2, C14.2, C15.2, C16.2, C17.2, C18.2, C20.2, J1.17, J10.1, R1.2, R2.1, R5.2, U1.A8, U1.C4, U1.D1, U1.D3, U1.D4, U1.E4, U1.E7, U1.F4, U1.F5, U1.F6, U2.11, U2.12, U2.17, U2.29, U2.30, U2.32, U3.4, U4.6, Y1.2, Y1.4
unnamed: C13.2, C19.2
unnamed: C14.1, U2.28
unnamed: C17.1, Y1.1
unnamed: C18.1, Y1.3
unnamed: D1.1, R5.1

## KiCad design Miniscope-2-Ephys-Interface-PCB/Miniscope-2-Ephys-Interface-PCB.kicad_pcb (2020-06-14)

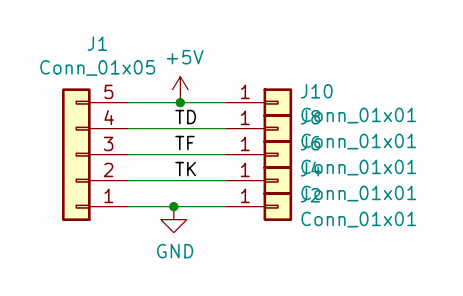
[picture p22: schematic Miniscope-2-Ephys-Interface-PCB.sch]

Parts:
J1: Conn_01x05; B2B_Flex_05_Dual_Row_38milx24mil_Hole_20mil_small
J2, J4, J6, J8, J10: Conn_01x01; Spring_2306654_3

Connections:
+5V: J1.5, J10.1
/TD: J1.4, J8.1
/TF: J1.3, J6.1
/TK: J1.2, J4.1
GND: J1.1, J2.1

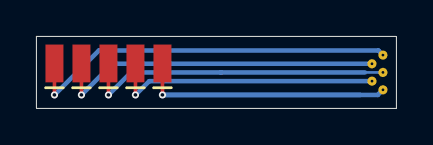
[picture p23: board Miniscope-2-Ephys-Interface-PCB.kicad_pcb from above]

Board: 2 copper layers, 20.0 x 4.0 mm, 6 parts (0 on the bottom side), 5 nets.

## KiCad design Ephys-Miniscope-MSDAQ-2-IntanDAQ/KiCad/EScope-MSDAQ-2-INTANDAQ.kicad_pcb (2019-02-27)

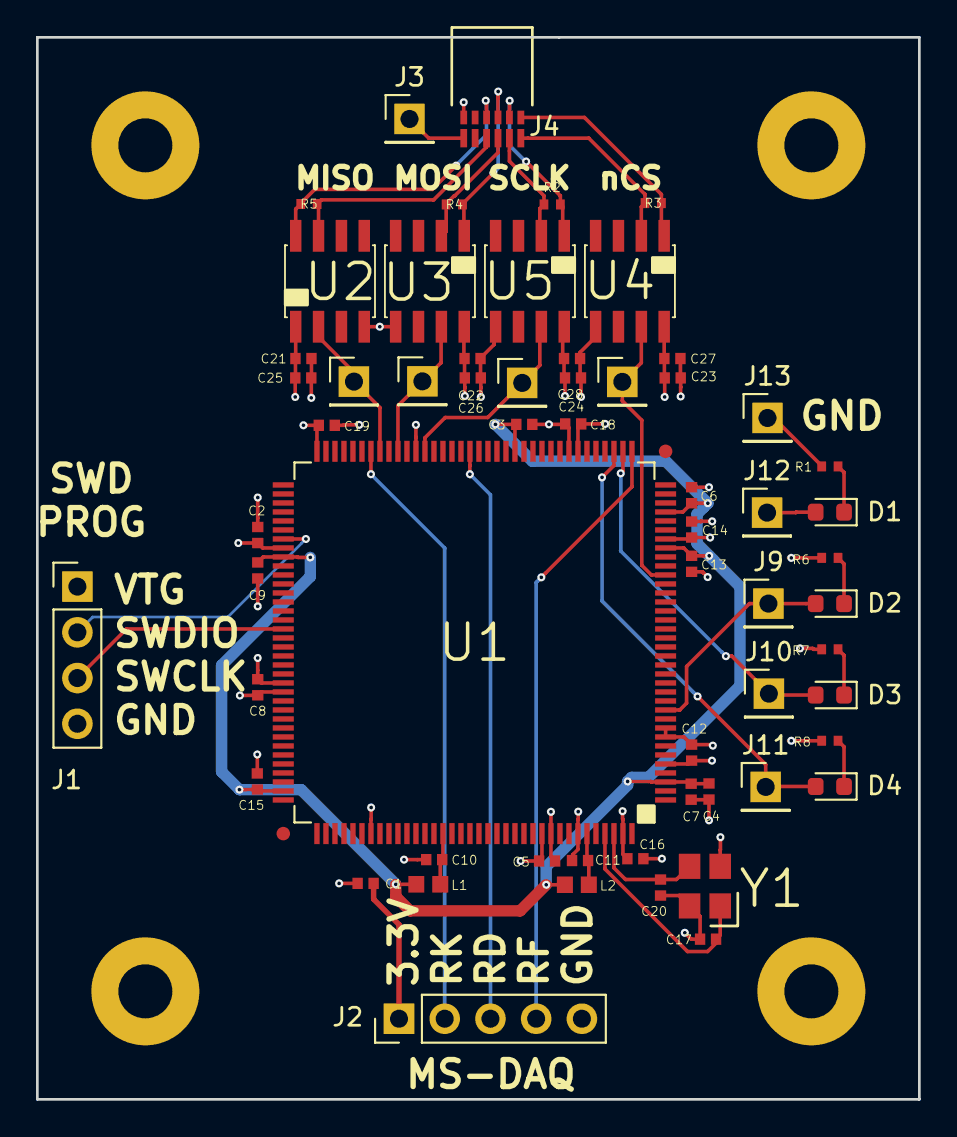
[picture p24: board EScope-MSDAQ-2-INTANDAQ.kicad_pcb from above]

Board: 4 copper layers, 49.0 x 59.0 mm, 65 parts (0 on the bottom side), 32 nets.

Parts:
C1: GRM155R60J106ME15D; C_0402_1005Metric_L
C2, C3, C5, C6, C7, C8, C9, C10, C11, C12, C13, C14, C15, C16, C18, C19, C21, C22, C23, C24: GRM155R71A104JA01D; C_0402_1005Metric_L
C4: GRM155R60J225KE95D; C_0402_1005Metric_L
C17, C20: GRM1555C1H120JA01D; C_0402_1005Metric_L
C25, C26, C27, C28: GRM155R71H102KA01D; C_0402_1005Metric_L
D1, D2, D3, D4: LED_Small_ALT; LED_0603_1608Metric
H1, H2, H3, H4: MountingHole_Pad; MountingHole_3mm_Pad
J1: Conn_01x04; PinHeader_1x04_P2.54mm_Vertical
J2: Conn_01x05; PinHeader_1x05_P2.54mm_Vertical
J3, J5, J6, J7, J8, J9, J10, J11, J12, J13: Conn_01x01; PinHeader_1x01_P2.54mm_Vertical
J4: A79623-001
L1, L2: BLM18PG471SN1D; L_0603_1608Metric_L
R1, R2, R3, R4, R5, R6, R7, R8: ERJ-2RKF1000X; R_0402_1005Metric_ERJ_L
U1: ATSAMV71Q21B-AABT; QFP_144_P50_2200X2200X160L60X22N
U2: DS90LV017A; SOIC_8_P127_490X600X175L83X41L
U3, U4, U5: DS90LV018A; SOIC_8_P127_490X600X175L83X41L
Y1: ABM8G-12.000MHZ-4Y-T3; OSCCC320X250X100L80X100

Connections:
+3V3: C1.1, C2.1, C5.1, C8.1, C12.1, C14.1, C16.1, C18.1, C19.1, C21.2, C22.1, C23.1, C24.1, C25.2, C26.1, C27.1, C28.1, D1.2, J1.1, J2.1, J12.1, U1.5, U1.30, U1.43, U1.72, U1.80, U1.96, U1.134, U1.143, U2.1, U3.8, U4.8, U5.8
/LED1: D2.2, J9.1, U1.11
/LED2: D3.2, J10.1, U1.38
/LED3: D4.2, J11.1, U1.39
/MCU_SPI_MISO: J8.1, U1.65, U2.2
/MCU_SPI_MOSI: J5.1, U1.63, U3.7
/MCU_SPI_NPCS: J6.1, U1.26, U4.7
/MCU_SPI_SPCK: J7.1, U1.60, U5.7
/MISO+: J4.7, R5.1, U2.7
/MISO-: J4.8, R5.2, U2.8
/MOSI+: J4.5, R4.2, U3.2
/MOSI-: J4.6, R4.1, U3.1
/RD: J2.2, U1.66
/RF: J2.3, U1.55
/RK: J2.4, U1.37
/SCLK+: J4.3, R2.2, U5.2
/SCLK-: J4.4, R2.1, U5.1
/SWCLK: J1.3, U1.89
/SWDIO: J1.2, U1.79
/VDDCORE: C3.1, C4.1, C6.1, C7.1, C9.1, C13.1, C15.1, L1.2, L2.2, U1.3, U1.29, U1.33, U1.50, U1.81, U1.107
/VDDPLL: C10.1, L1.1, U1.123
/VDDUTMIC: C11.1, L2.1, U1.139
/XIN: C17.1, U1.141, Y1.1
/XOUT: C20.1, U1.142, Y1.3
/nCS+: J4.1, R3.2, U4.2
/nCS-: J4.2, R3.1, U4.1
GND: C1.2, C2.2, C3.2, C4.2, C5.2, C6.2, C7.2, C8.2, C9.2, C10.2, C11.2, C12.2, C13.2, C14.2, C15.2, C16.2, C17.2, C18.2, C19.2, C20.2, C21.1, C22.2, C23.2, C24.2, C25.1, C26.2, C27.2, C28.2, H1.1, H2.1, H3.1, H4.1, J1.4, J2.5, J4.12, J13.1, R1.1, R6.1, R7.1, R8.1, U1.8, U1.9, U1.44, U1.61, U1.95, U1.115, U1.135, U1.138, U2.4, U3.5, U4.5, U5.5, Y1.2, Y1.4
unnamed: D1.1, R1.2
unnamed: D2.1, R6.2
unnamed: D3.1, R7.2
unnamed: D4.1, R8.2
unnamed: J3.1, J4.11

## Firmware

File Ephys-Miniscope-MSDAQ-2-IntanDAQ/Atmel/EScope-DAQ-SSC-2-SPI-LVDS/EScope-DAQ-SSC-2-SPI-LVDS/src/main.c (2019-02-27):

/**
 * \file
 *
 * \brief Empty user application template
 *
 */

/**
 * \mainpage User Application template doxygen documentation
 *
 * \par Empty user application template
 *
 * Bare minimum empty user application template
 *
 * \par Content
 *
 * -# Include the ASF header files (through asf.h)
 * -# "Insert system clock initialization code here" comment
 * -# Minimal main function that starts with a call to board_init()
 * -# "Insert application code here" comment
 *
 */

/*
 * Include header files for all drivers that have been imported from
 * Atmel Software Framework (ASF).
 */
/*
 * Support and FAQ: visit <a href="http://www.atmel.com/design-support/">Atmel Support</a>
 */
#include <asf.h>

//------------- Definitions -----------
//RHD2132 Reg Definitions
#define CALIBRATE							0b0101010100000000 //Inits self cal routine
#define CLEAR								0b0110101000000000 //Clears on chip cal parameters
#define REG_ADC_CONFIG_AND_FAST_SETTLE		0
#define REG_SUPPLY_SENSOR_AND_BIAS_CURRENT	1
#define REG_MUX_BIAS_CURRENT				2
#define REG_MUX_LOAD						3
#define REG_ADC_OUTPUT_FORMAT_DSP_OFFSET	4
#define REG_IMPEDANCE_CHECK_CONTROL			5
#define REG_IMPEDANCE_CHECK_DAC				6
#define REG_IMPEDANCE_CHECK_AMP_SELECT		7
#define REG_AMP_BANDWIDTH_1					8
#define REG_AMP_BANDWIDTH_2					9
#define REG_AMP_BANDWIDTH_3					10
#define REG_AMP_BANDWIDTH_4					11
#define REG_AMP_BANDWIDTH_5					12
#define REG_AMP_BANDWIDTH_6					13
#define REG_AMP_POWER_1						14
#define REG_AMP_POWER_2						15
#define REG_AMP_POWER_3						16
#define REG_AMP_POWER_4						17

#define RHD_REG_BIT							0x8000
#define RHD_READ_BIT						0x4000

// ------- LEDs on Board
#define LED1_PIN			PIO_PC0_IDX
#define LED2_PIN			PIO_PC1_IDX
#define LED3_PIN			PIO_PC2_IDX
// ------- SSC Definitions
#define RD_PIN				PIO_PA10_IDX
#define RD_MODE				IOPORT_MODE_MUX_C
#define RF_PIN				PIO_PD24_IDX
#define RF_MODE				IOPORT_MODE_MUX_B
#define RK_PIN				PIO_PA22_IDX
#define RK_MODE				IOPORT_MODE_MUX_A

// ------- SSC DMA
#define SSC_XDMAC_RX_CH_NUM	33 //Actual DMA channel ID for SSC
#define SSC_XDMAC_RX_CH		0 //Specific DMA channel used for this communication (0 and 1 are taken by SPI0)

#define SSC_DMA_OFF			0
#define SSC_DMA_ON			1

// ------- SPI Definitions
#define SPI_SLAVE_BASE		SPI0
#define SPI_IRQn			SPI0_IRQn
#define SPI_ID				ID_SPI0

#define SPI_CHIP_SEL		0
#define SPI_CHIP_PCS		spi_get_pcs(SPI_CHIP_SEL)
#define SPI_CLK_POLARITY	0
#define SPI_CLK_NPHASE		1
#define SPI_DLYBS			0x0 //Delay between NPCS activation to first SPCK (0 is half clock cycle)
#define SPI_DLYBCT			0x01 //Delay between consecutive transfers. A delay before CS is pulled up at end of transfer
#define SPI_DLYBCS			0x10 // Delay NPCS is held high before next transmit
#define SPI_CLK_RATE		10000000//24000000

#define SPI_MISO_PIN		PIO_PD20_IDX
#define SPI_MISO_MODE		IOPORT_MODE_MUX_B
#define SPI_MOSI_PIN		PIO_PD21_IDX
#define SPI_MOSI_MODE		IOPORT_MODE_MUX_B
#define SPI_SPCK_PIN		PIO_PD22_IDX
#define SPI_SPCK_MODE		IOPORT_MODE_MUX_B
#define SPI_NPCS_PIN		PIO_PB2_IDX
#define SPI_NPCS_MODE		IOPORT_MODE_MUX_D

//Other Definitions
#define EPHYS_FRAME_START				0xA83C42FA

#define EPHYS_NUM_CHAN					32
#define EPHYS_SSC_SAMP_PER_PACKET		1
#define MAX_WORDS_IN_HEADER				4
#define MAX_WORDS_IN_DATA_PACKET		EPHYS_NUM_CHAN*EPHYS_SSC_SAMP_PER_PACKET

//Functions

// ------------ Global Vars -----------
static xdmac_channel_config_t ssc_xdmac_rx_cfg; //XDMAC channel configuration.
volatile uint32_t words_in_header		= 0; //4; //????
volatile uint32_t words_in_data_packet	= 32;
volatile uint16_t RHD_reg_value[256] = {0}; //Holds a copy of all RHD2132 reg values
volatile uint16_t RHD_ADC_value[MAX_WORDS_IN_HEADER+MAX_WORDS_IN_DATA_PACKET] = {0}; //Holds last sampled ADC value

volatile uint16_t packet_num = 0;
volatile uint16_t num_packets_received = 0;
volatile uint16_t spi_miso_next_data = 0; //Holds upcoming MISO output words

// Testing vars
volatile uint16_t testCh = 0;

volatile uint16_t spi_tx[35] = {0};
volatile uint16_t spi_tx_idx = 0;

volatile uint16_t spi_rx[35] = {0};
volatile uint16_t spi_rx_idx = 0;

// ---------- Functions ----------
void fill_RHD_reg_value_array(void);
uint8_t RHD_get_reg_from_command(uint16_t);
uint8_t RHD_get_channel_from_command(uint16_t);
uint8_t RHD_get_value_from_command(uint16_t);
uint16_t spi_handle_command(uint16_t );
void spi_slave_init(void);
void ssc_init(void);
void ssc_xdmac_configure(void);
void ssc_disable_xdmac(void);
void ssc_enable_xdmac(void);
// ------------------------------------

void fill_RHD_reg_value_array(void) {
	//Don't currently have default values for reg. Hopefully I don't need them
	RHD_reg_value[0b11000000|40] = 'I';
	RHD_reg_value[0b11000000|41] = 'N';
	RHD_reg_value[0b11000000|42] = 'T';
	RHD_reg_value[0b11000000|43] = 'A';
	RHD_reg_value[0b11000000|44] = 'N';
	
	RHD_reg_value[0b11000000|48] = 'R'; // From Intan source code
	RHD_reg_value[0b11000000|49] = 'H'; // From Intan source code
	RHD_reg_value[0b11000000|50] = 'D'; // From Intan source code
	
	//RHD_reg_value[40] = ; //Die revision
	RHD_reg_value[0b11000000|59] = 0; // For RHD2132 found in Intan source code
	RHD_reg_value[0b11000000|61] = 1; //Unipolar amps
	RHD_reg_value[0b11000000|62] = 32; //Number of amps on chip
	RHD_reg_value[0b11000000|63] = 1; //RHD2132 chip ID
	
}

uint8_t RHD_get_reg_from_command(uint16_t command) {
	return (0x3F&(command>>8));
}

uint8_t RHD_get_channel_from_command(uint16_t command) {
	return (0x3F&(command>>8));
}

uint8_t RHD_get_value_from_command(uint16_t command) {
	return (0xFF&command);
}

uint16_t spi_handle_command(uint16_t command) {
	//This will return what the Intan DAQ is expecting to get from the MISO line
	volatile uint8_t testComm;
	volatile uint16_t outValue = 0;
	
	// Testing data in and out of spi
	//spi_tx[spi_tx_idx] = spi_miso_next_data;
	//spi_tx_idx++;
	//if (spi_tx_idx >= 35) {
	//spi_tx_idx = 0;
	//}
	//spi_rx[spi_rx_idx] = command;
	//spi_rx_idx++;
	//if (spi_rx_idx >= 35) {
	//spi_rx_idx = 0;
	//}
	// ===============================
	
	if ((command&(RHD_READ_BIT|RHD_REG_BIT)) == 0) {
		//Convert command
		//RHD_ADC_value[RHD_get_channel_from_command(command)+words_in_header]++;
		testComm = RHD_get_channel_from_command(command);
		if ((testComm == 1) || (testComm == 9)) {
			testCh++;
			outValue = testCh;
		}
		else {
			outValue = (RHD_ADC_value[testComm+words_in_header]);
		}
	}
	else if (command&RHD_REG_BIT){
		//Will be reading or writing to a reg in RHD
		if (command&RHD_READ_BIT) {
			//Will be reading an RHD reg
			outValue = (RHD_reg_value[RHD_get_reg_from_command(command)]);
		}
		else {
			//Will be writing to an RHD reg
			//We are going to fake a write
			RHD_reg_value[RHD_get_reg_from_command(command)] = RHD_get_value_from_command(command);
			outValue = (0xFF00 | RHD_get_value_from_command(command));
		}
	}
	else {
		//Handles all non-read/write commands
		switch (command)
		{
			case (CALIBRATE):
			//Should actually return this on this and following 9 commands
			outValue = (0x0000); //Will be 0x8000 is expecting 2's complement
			break;
			case (CLEAR):
			outValue = (0x0000); //Will be 0x8000 is expecting 2's complement
			break;
		}
	}
	return outValue; // Should never get here
}

void spi_slave_init(void) {
	//Need to shift from Master to Slave !!!!
	ioport_set_pin_mode(SPI_MISO_PIN,SPI_MISO_MODE);
	ioport_disable_pin(SPI_MISO_PIN);
	ioport_set_pin_mode(SPI_MOSI_PIN,SPI_MOSI_MODE);
	ioport_disable_pin(SPI_MOSI_PIN);
	ioport_set_pin_mode(SPI_SPCK_PIN,SPI_SPCK_MODE);
	ioport_disable_pin(SPI_SPCK_PIN);
	ioport_set_pin_mode(SPI_NPCS_PIN,SPI_NPCS_MODE);
	ioport_disable_pin(SPI_NPCS_PIN);
	
	pmc_enable_periph_clk(SPI_ID);

	SPI_SLAVE_BASE->SPI_CR = SPI_CR_SPIDIS; //Disabled SPI
	SPI_SLAVE_BASE->SPI_CR = SPI_CR_SWRST; //Resets SPI
	//SPI_SLAVE_BASE->SPI_CR = SPI_CR_LASTXFER; //De-asserts NPCS after every TD transfer
	//SPI_SLAVE_BASE->SPI_MR |= SPI_MR_MSTR; //Sets to master mode
	SPI_SLAVE_BASE->SPI_MR |= SPI_MR_MODFDIS; //Disables fault detection
	
	// Sets Peripheral Chip Select
	SPI_SLAVE_BASE->SPI_MR &= (~SPI_MR_PCS_Msk); //Empties out the PCS bits
	SPI_SLAVE_BASE->SPI_MR |= SPI_MR_PCS(SPI_CHIP_PCS); //Sets the PCS bits
	
	// Sets Polarity
	if (SPI_CLK_POLARITY) {
		SPI_SLAVE_BASE->SPI_CSR[SPI_CHIP_SEL] |= SPI_CSR_CPOL; //1
	}
	else {
		SPI_SLAVE_BASE->SPI_CSR[SPI_CHIP_SEL] &= (~SPI_CSR_CPOL); //0
	}
	
	// Sets Phase
	if (SPI_CLK_NPHASE) {
		SPI_SLAVE_BASE->SPI_CSR[SPI_CHIP_SEL] |= SPI_CSR_NCPHA; //1
	}
	else {
		SPI_SLAVE_BASE->SPI_CSR[SPI_CHIP_SEL] &= (~SPI_CSR_NCPHA); //0
	}
	
	// Peripheral chip select line rises after each transfer for a minimum of DLYBCS
	//SPI_SLAVE_BASE->SPI_CSR[SPI_CHIP_SEL] |= SPI_CSR_CSNAAT;
	
	//Bits Per Transfer
	SPI_SLAVE_BASE->SPI_CSR[SPI_CHIP_SEL] &= (~SPI_CSR_BITS_Msk);
	SPI_SLAVE_BASE->SPI_CSR[SPI_CHIP_SEL] |= SPI_CSR_BITS_16_BIT;

	//Set BAUD rate div CHECK ACTUAL SCLK OUTPUT!!!
	//SPI_SLAVE_BASE->SPI_CSR[SPI_CHIP_SEL] &= (~SPI_CSR_SCBR_Msk);
	//SPI_SLAVE_BASE->SPI_CSR[SPI_CHIP_SEL] |= SPI_CSR_SCBR(sysclk_get_peripheral_hz()/ SPI_CLK_RATE);

	//Set Delays
	//SPI_SLAVE_BASE->SPI_CSR[SPI_CHIP_SEL] &= ~(SPI_CSR_DLYBS_Msk | SPI_CSR_DLYBCT_Msk);
	//SPI_SLAVE_BASE->SPI_CSR[SPI_CHIP_SEL] |= SPI_CSR_DLYBS(SPI_DLYBS) | SPI_CSR_DLYBCT(SPI_DLYBCT);
	
	//Sets Delay of NPCS is held high between transfers
	//SPI_SLAVE_BASE->SPI_MR &= (~SPI_MR_DLYBCS_Msk);
	//SPI_SLAVE_BASE->SPI_MR |= SPI_MR_DLYBCS(SPI_DLYBCS);
	
	//Set up interrupts
	SPI_SLAVE_BASE->SPI_IER = SPI_IER_RDRF | SPI_IER_TDRE; //SPI receive reg full interrupt
	SPI_SLAVE_BASE->SPI_CR = SPI_CR_SPIEN; //Enable SPI!
	
	
}

void ssc_init(void) {
	ioport_set_pin_mode(RD_PIN,RD_MODE);
	ioport_disable_pin(RD_PIN);
	ioport_set_pin_mode(RF_PIN,RF_MODE);
	ioport_disable_pin(RF_PIN);
	ioport_set_pin_mode(RK_PIN,RK_MODE);
	ioport_disable_pin(RK_PIN);
	
	pmc_enable_periph_clk(ID_SSC);
	ssc_reset(SSC);
	
	SSC->SSC_CR = SSC_CR_RXDIS; //Disables SSC Rx
	
	//SSC->SSC_CMR = ?; //Clock divider?
	//Receiver clock settings
	SSC->SSC_RCMR = (SSC_RCMR_CKS_RK | //Use RK pin as input clock
	SSC_RCMR_CKI | //Sampled on rising edge
	SSC_RCMR_STTDLY(16) |
	SSC_RCMR_START_RF_RISING); //Sets start trigger
	//SSC->SSC_RFMR = (SSC_RFMR_DATLEN(31) | //(SSC_RFMR_DATLEN(15) | //Data bit length
	//				SSC_RFMR_DATNB(15) |
	//				SSC_RFMR_MSBF);
	SSC->SSC_RFMR = (SSC_RFMR_DATLEN(31) | //(SSC_RFMR_DATLEN(15) | //Data bit length
	SSC_RFMR_FSLEN(15) | //Putting 16bit sync to hold packet number
	SSC_RFMR_DATNB(15) |
	SSC_RFMR_MSBF);
	
	SSC->SSC_CR |= SSC_CR_RXEN; //Transmit Enable
}

void ssc_xdmac_configure(void) {


	/* Initialize channel config for receiver */
	ssc_xdmac_rx_cfg.mbr_ubc = (words_in_header+words_in_data_packet)/2; //ssc_xdmac_rx_cfg.mbr_ubc = words_in_header+words_in_data_packet;

	ssc_xdmac_rx_cfg.mbr_sa = (uint32_t)&(SSC->SSC_RHR);
	ssc_xdmac_rx_cfg.mbr_da = (uint32_t)&RHD_reg_value[0];
	ssc_xdmac_rx_cfg.mbr_cfg = XDMAC_CC_TYPE_PER_TRAN |
	XDMAC_CC_MBSIZE_SINGLE |
	XDMAC_CC_DSYNC_PER2MEM |
	XDMAC_CC_CSIZE_CHK_1 |
	XDMAC_CC_DWIDTH_WORD | //XDMAC_CC_DWIDTH_HALFWORD |
	XDMAC_CC_SIF_AHB_IF1 |
	XDMAC_CC_DIF_AHB_IF0 |
	XDMAC_CC_SAM_FIXED_AM |
	XDMAC_CC_DAM_INCREMENTED_AM |
	XDMAC_CC_PERID(SSC_XDMAC_RX_CH_NUM);

	ssc_xdmac_rx_cfg.mbr_bc = 0;
	ssc_xdmac_rx_cfg.mbr_ds =  0;
	ssc_xdmac_rx_cfg.mbr_sus = 0;
	ssc_xdmac_rx_cfg.mbr_dus = 0;

	xdmac_configure_transfer(XDMAC, SSC_XDMAC_RX_CH, &ssc_xdmac_rx_cfg);
	
	xdmac_channel_set_descriptor_control(XDMAC, SSC_XDMAC_RX_CH, 0);
	xdmac_channel_enable_interrupt(XDMAC, SSC_XDMAC_RX_CH, XDMAC_CIE_BIE);
	xdmac_enable_interrupt(XDMAC,SSC_XDMAC_RX_CH);
	//xdmac_channel_enable(XDMAC, SSC_XDMAC_RX_CH);
	
	
}

void ssc_enable_xdmac(void) {
	
	SCB_CleanInvalidateDCache();
	XDMAC->XDMAC_GE = (XDMAC_GE_EN0 << SSC_XDMAC_RX_CH);
	
	
}

void ssc_disable_xdmac(void) {
	//Taken from SPI DMA disable function. Might need changing
	xdmac_channel_disable(XDMAC, SSC_XDMAC_RX_CH);
}
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

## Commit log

2019-02-27 Add initial files
    Porting Ephys Miniscope SSC 2 LVDS SPI over from a separate git repo.
    [EScope-MSDAQ-2-INTANDAQ-B.Cu.gbr, EScope-MSDAQ-2-INTANDAQ-B.Mask.gbr, EScope-MSDAQ-2-INTANDAQ-B.Paste.gbr, EScope-MSDAQ-2-INTANDAQ-B.SilkS.gbr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]
2019-03-19 Correct SWD pin labels in pictures
2020-06-11 Rearrange project and edit schematic with some corrections and notes.
    [BOM_PartType-Miniscope 32ch Ephys.xlsx, Ephys_PCB_top.kicad_pcb, Ephys_PCB_top.sch, Ephys_PCB_top_updated.kicad_pcb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]
2020-06-13 Update schematic and footprints
    * Replaced MCU symbol, pinout, and footprint with correct one (TFBGA version).
    * Created and replaced slimstack connector with the correct one.
    * Replaced crystal oscillator with better symbol
    * Tried to link as many footprints as possible to those contained in the Aharoni KiCad Library.
    * TODO: Add transistor to drive status LED.
    [Ephys_PCB_top_updated.kicad_pcb, Ephys_PCB_top_updated.sch]
2020-06-13 Group components in PCB layout
    [Ephys_PCB_top_updated.kicad_pcb, Ephys_PCB_top_updated.sch]
2020-06-13 Update Board Setup Specifications
    Via: 0.15mm/0,3mm
    Trace/Space: 3mil/3mil
    [Ephys_PCB_top_updated.kicad_pcb, Ephys_PCB_top_updated.sch]
2020-06-13 Switch to 6 layer PCB
    [Ephys_PCB_top_updated.kicad_pcb]
2020-06-13 Move things around in PCBnew and add prelim board outline.
    [Ephys_PCB_top_updated.kicad_pcb, Ephys_PCB_top_updated.sch]
2020-06-14 Add a prototype Miniscope to Ephys PCB connector PCB
    [Miniscope-2-Ephys-Interface-PCB.kicad_pcb, Miniscope-2-Ephys-Interface-PCB.sch]
2020-06-14 Change display layers for designators and footprint info.
    [Ephys_PCB_top_updated.kicad_pcb]
2020-06-14 Move around PCB layout a bit and initial route of electrode traces.
    [Ephys_PCB_top_updated.kicad_pcb]
2020-06-15 Move to new KiCad project for multi-board Ephys layout
    [Connector-Interface.sch, Ephys.sch, Ephys_PCB_top_updated.kicad_pcb, Ephys_PCB_top_updated.sch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]
2020-06-15 Finish initial PCB layout.
    [Miniscope-V4-Ephys-System.kicad_pcb]
2020-06-15 Finish layout of MCU PCB and routing of almost all traces.
    [MCU.sch, Miniscope-V4-Ephys-System.kicad_pcb]
2020-06-15 Change orientation of some components and add notes to PCB layout
    [Miniscope-V4-Ephys-System.kicad_pcb]
2020-06-16 Switch to female slimstack and reorder pins to batch 32ch silicon probe connector
    [Connector-Interface.sch, Ephys.sch, Miniscope-V4-Ephys-System.kicad_pcb]
2020-06-16 Finish routing Ephys and Connector PCBs. Decrease layer count to 4.
    [Ephys.sch, Miniscope-V4-Ephys-System.kicad_pcb]
2020-06-16 Finish routing of all PCBs. Need to double check before fabrication.
    [MCU.sch, Miniscope-V4-Ephys-System.kicad_pcb]
2020-06-26 Revert "pcb file updated"
    [Miniscope-V4-Ephys-System.kicad_pcb]
2020-06-30 Add mouse bites and panel the 3 PCBs.
    [Miniscope-V4-Ephys-System.kicad_pcb]
2020-07-08 Revert "updated ephys pcb with low profile connectors and started programming board"
    [Miniscope-V4-Ephys-System.kicad_pcb]
2020-07-08 Remove paste on connector pads on ephys and connector PCB
    [Miniscope-V4-Ephys-System.kicad_pcb]
2020-07-08 Switch spring connectors to a lower profile option
    [MCU.sch, Miniscope-V4-Ephys-System.kicad_pcb]
2020-07-08 Add programing board and generate GERBERS for fab (v0.1)
    [Miniscope-V4-Ephys-System-B_Cu.gbr, Miniscope-V4-Ephys-System-B_Mask.gbr, Miniscope-V4-Ephys-System-B_Paste.gbr, Miniscope-V4-Ephys-System-B_SilkS.gbr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]
2020-07-16 Add all fab files for first PCB fab run of this design. v0.1 at PCBway.
    [Connector-Interface.sch, Ephys.sch, MCU.sch, Miniscope-V4-Ephys-System-B_Cu.gbr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]
